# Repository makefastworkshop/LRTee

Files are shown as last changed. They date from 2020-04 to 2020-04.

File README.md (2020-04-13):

# LRTee: 3D Printed Ventilator Splitter
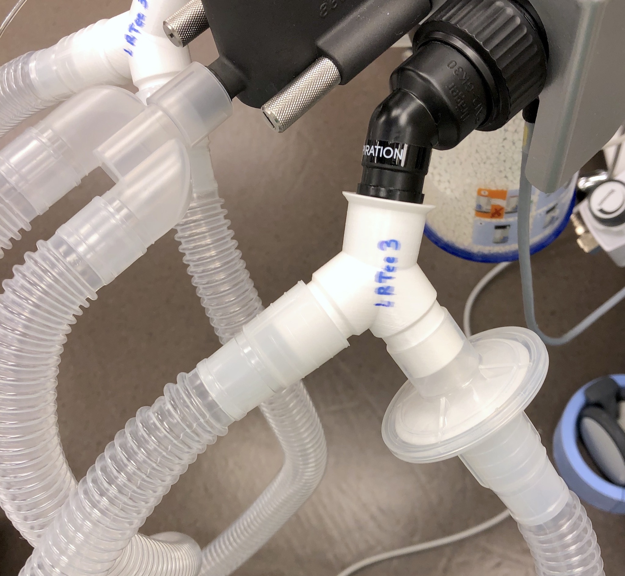
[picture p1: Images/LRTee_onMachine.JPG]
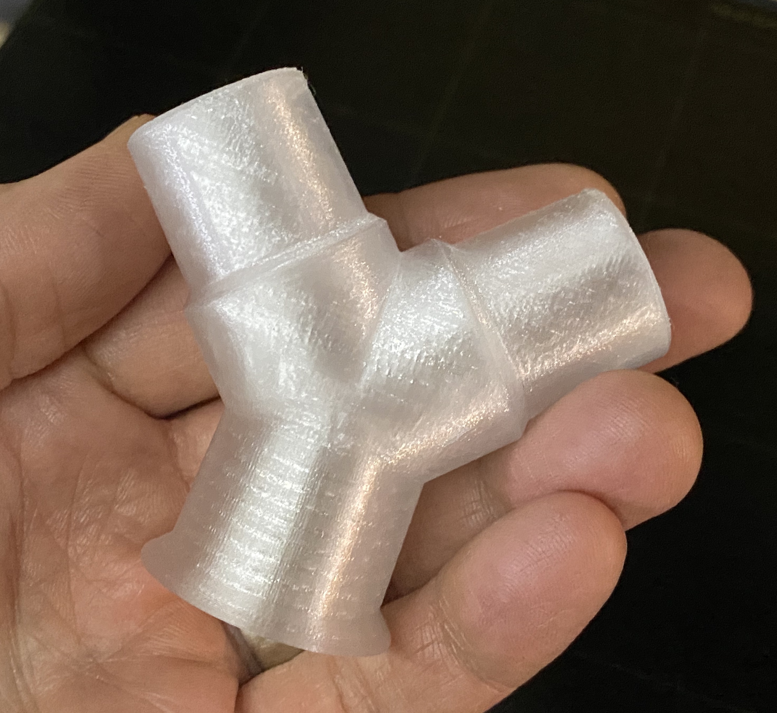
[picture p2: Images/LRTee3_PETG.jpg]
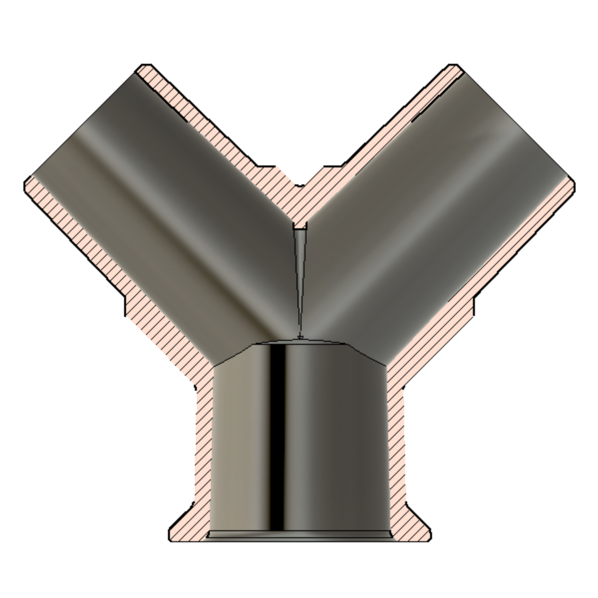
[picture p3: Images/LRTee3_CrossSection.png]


**LRTee is a 3D printed ventilator splitter** with standard 22mm tubing connectors to be used only in the event of Emergency Use Authorization when there is no more ventilator capacity.

Unlike other splitters, LRTee is designed to print on a standard FFF/FDM 3D printer without the need for supports/rafts and is optimized for creating an air-tight part that can pass a ventilator system's automated leak test without the need for post processing.

LRTee is released as public domain (Creative Commons Zero v1.0 Universal) for anyone to use, modify, share, produce, etc. with no strings attached.

## Background

Patients with COVID-19 in serious or critical condition often require assisted breathing via ventilator. As the number of patients in need of ventilators grows (exponentially in many densely populated regions), there are not adequate numbers of ventilators to support the high number of patients.

This is an EXPERIMENTAL splitter for 22m tubing to allow two patients to share a single ventilator. After printing/testing multiple versions of other splitter designs (see below) we decided to build a new splitter that:

* Has uniformly thicker walls.
* Has shorter branches (less likely to break).
* Is much faster to print (under 4 hours to print a usable pair or LRTee parts).
* Doesn't require supports or rafts.
* Can be scaled to handle basic low-temp sterilization (use 101-102% for PLA).
* **Released as Public Domain** (CC0) with all design files for further modifications.

## Disclaimer

As with other similar efforts, **THIS IS UNCERTIFIED, HIGHLY EXPERIMENTAL, and UNTESTED ON HUMANS**. As such, any potential use scenario would also require **legal waivers to use uncertified/untested non-medical devices** and **significant additional patient monitoring by medical professionals and certified diagnostic equipment** to reduce the risk of serious consequences in the event that the device fails to operate as intended by doctors. Use at your own risk. We take no responsibility for the safety of this device/design. 

These parts have been test-fit on anesthesia machines with ventilator capabilities and standard 22mm ventilator tubing/circuit connectors. The parts should be able to pass the system's automated "leak test" directly off the printer with no post-processing.

## Supplying LRTee to Hospitals

If you intend to print LRTee splitters and supply them to local hospitals, we recommend following these steps:

* First, contact the hospital by phone where you intend to supply the parts and see if they are needed/wanted as a last resort.
* Assume you are infected and act accordingly at all times (COVID-19 can be asymptomatic for some people, and protecting hospital staff is critically important). Wash hands and don't handle any more than necessary.
* Use the highest quality PETG or PLA you have. Using pure/uncolored materials is best to limit the addition of other unspecified compounds in the plastic.
* Make a test print. Depending on your printer's setup, you may need to tune settings to get the best print possible.
* Print the associated parts as specified. Note that it takes two (2) splitters for each additional patient, so it's logical to print and supply them in pairs.
* When the parts are finished, try to knock off any burrs, globs, or stringing that could interfere with their operation. You may also be able to gently fit the parts into each other and twist to get a sense for how smoothly the connectors fit.
* Place in a sealable/zip-top plastic bag.
* Print and fill out a form to help the hospital and make certain that you, as a maker trying to help, cannot be held liable (see [LRTee - Hospital Intake Printout.pdf](https://github.com/makefastworkshop/LRTee/blob/master/Docs/LRTee%20-%20Hospital%20Intake%20Printout.pdf)).
* Place signed and dated form in the bag with the parts and seal.
* Call ahead and schedule a drop off to appropriate medical personnel.

## Print Instructions

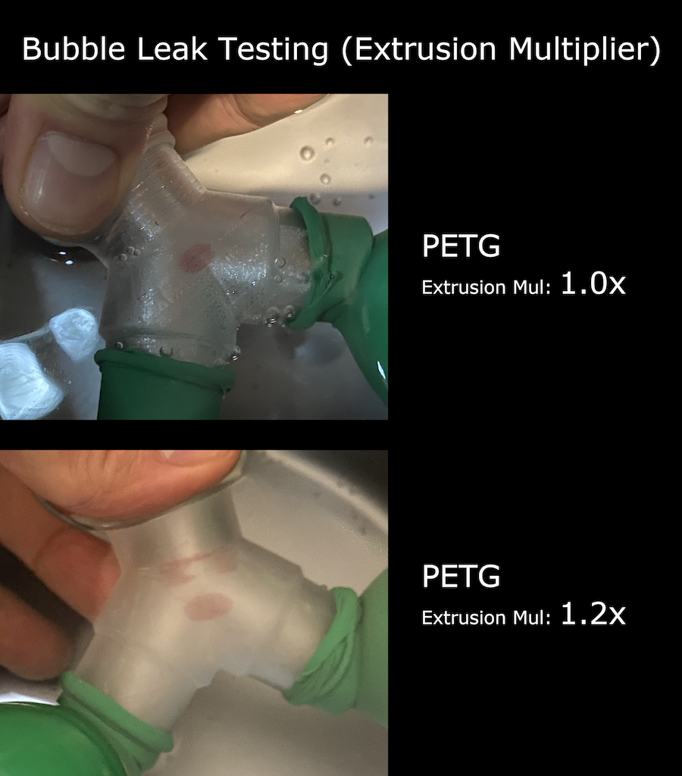
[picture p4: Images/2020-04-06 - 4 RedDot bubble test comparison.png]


This part is designed to be printed in either PETG (recommended) or PLA. When sterilized, either of these materials are likely to be usable in last-resort circumstances.

While the parts should print very cleanly, it's good to double check that all fittings are clean and free of extraneous globs of materials to ensure the best connection possible. 

The parts should be able to pass the ventilator system's automated "leak test" directly off the printer with no post-processing needed.

Infill of 100% should be achieved by using a very high number of perimeters that force smooth, solid printing throughout the build.

### Printing in PETG

Printing in natural/clear PETG is recommended due to its slightly more flexible nature, toughness, and resistance to elevated temperatures (up to 75C without significant shrinkage/warping).

We've also found that PETG seems to print slightly less air-tight than PLA, but this can be greatly improved by over-extruding. Setting the "extrusion multiplier" to 1.2x (and using the associated STL file that compensates slightly for the increased print size) produces a much more air-tight part.

### Printing in PLA

Note that PLA is harder and will shrink more (when heated/sterilized) than PETG. As such, if printed in PLA a sterilization "bath" may be preferred instead of using a low-temp sterilization machine (which seems to still get up to 60C or more) to keep the part from shrinking beyond tolerances for an air-tight fit. If a PLA part will be sterilized (for example, with a low-temp VHP machine), printing at 101-102% is suggested so that the part is properly sized after shrinking.

See the image above for a comparison of shrinkage characteristics along critical dimensions for various annealing temperatures. 

## Prior Work / Reference

The general theory of using a splitter to ventilate multiple patients is nicely spelled out in [COVID-19 How to Use One Ventilator to Save Multiple Lives](https://www.youtube.com/watch?v=uClq978oohY) and [A Single Ventilator for Multiple Simulated Patients to Meet Disaster Surge](https://onlinelibrary.wiley.com/doi/epdf/10.1197/j.aem.2006.05.009).

Thanks to these projects for informing/sharing/catalyzing design and discussion to yield a usable, printable splitter.
* [3D Printed Circuit Splitter and Flow Restriction Devices for Multiple Patient Lung Ventilation](https://www.prusaprinters.org/prints/25808-3d-printed-circuit-splitter-and-flow-restriction-d)
* [Ventilator Circuit Splitters - reinforced & thicker walls](https://www.prusaprinters.org/prints/27803-ventilator-circuit-splitters-reinforced-thicker-wa)

## Changes

**Update April 5, 2020**: More testing with annealing (via hot water bath) to simulate sterilization temperatures was performed and added as a graph (see image). Added a small rise to the lower/female lip to soften the sharp corner, and now including a PETG printer config that seems to produce good results.

**Update April 7, 2020**: We've found that PLA seems to print a bit more air-tight than PETG, but that can be greatly improved by setting the "extrusion multiplier" to 1.2x and using the modified STL file that compensates for the slightly larger dimensions when printed.

**Update April 8, 2020**: Produced 4 pairs in PETG with 1.2x extrusion multiplier and ran through the full process (from intake of printed parts at a medical facility, thorough cleaning/decontamination/sanitization, and finally testing on ventilators to verify it passes the leak test).  Parts show no sign of deformation or failure and pass all primary initial tests.

**Update April 10, 2020**: Added concise documentation to help medical facilities replicate the intake/cleaning/testing process. See the "Supplying LRTee to Hospitals" section above.

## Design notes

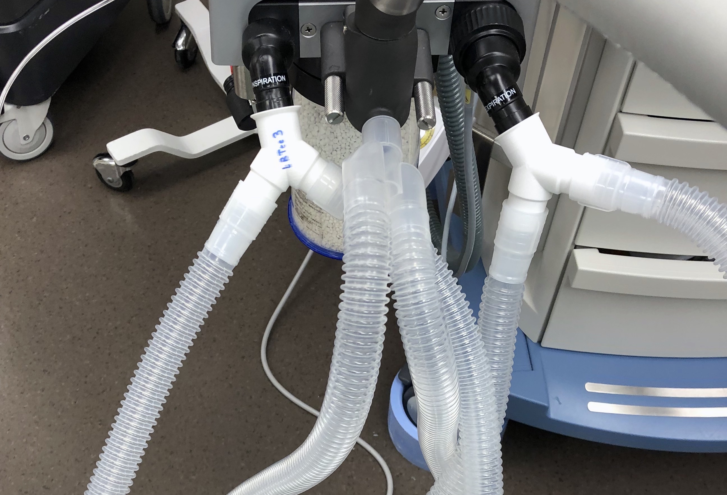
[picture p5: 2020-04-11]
Images/LRTee_onMachine2.JPG

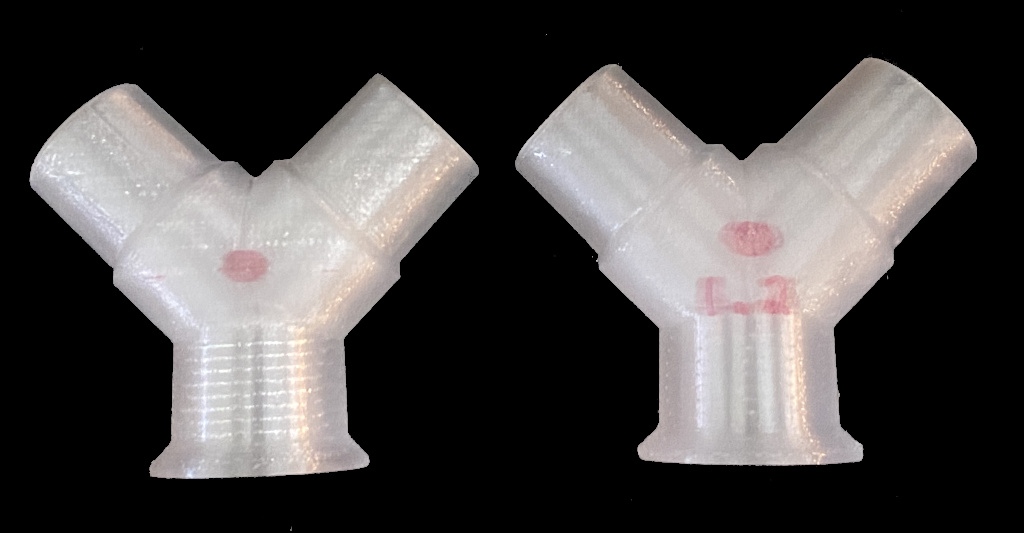
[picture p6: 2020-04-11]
Images/2020-04-06 - 1 RedDot vs OverExtrude120.jpg

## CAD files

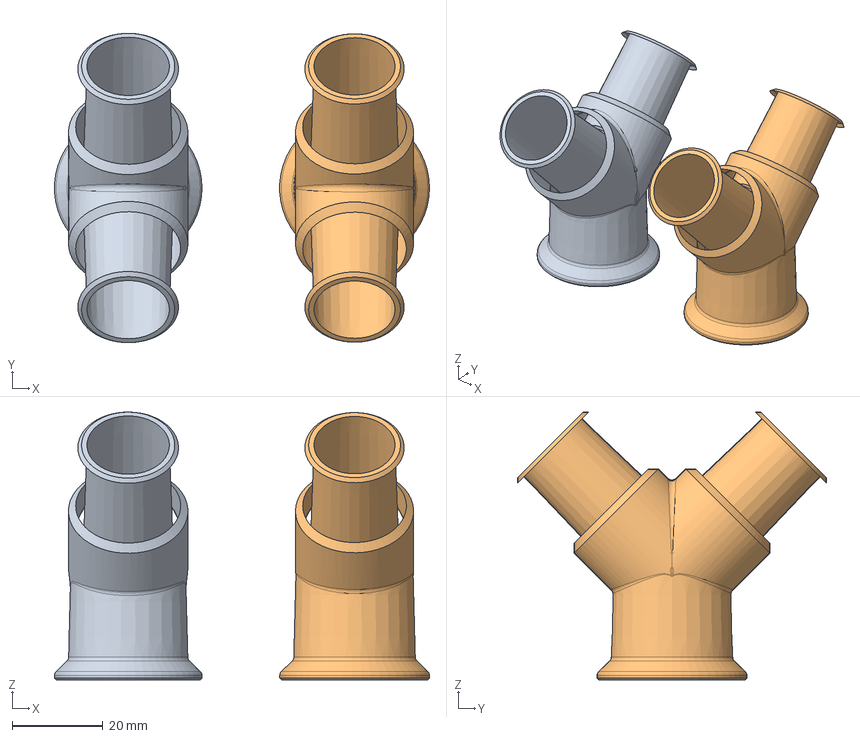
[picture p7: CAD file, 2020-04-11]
CAD/LRTee3_CAD.step
82.8 x 68.3 x 59.2 mm
LRTee3
LRTee3_ExtrudeAt1.2x

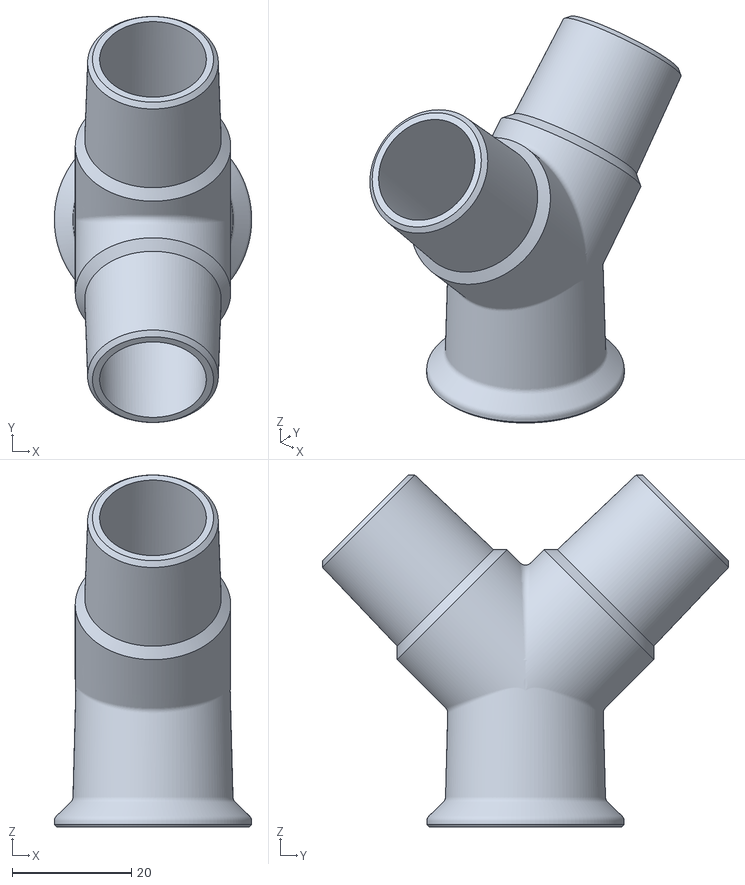
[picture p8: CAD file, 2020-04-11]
PrintFiles/LRTee3_PrintExtrudeAt12x.stl
33.1 x 68.1 x 59.1

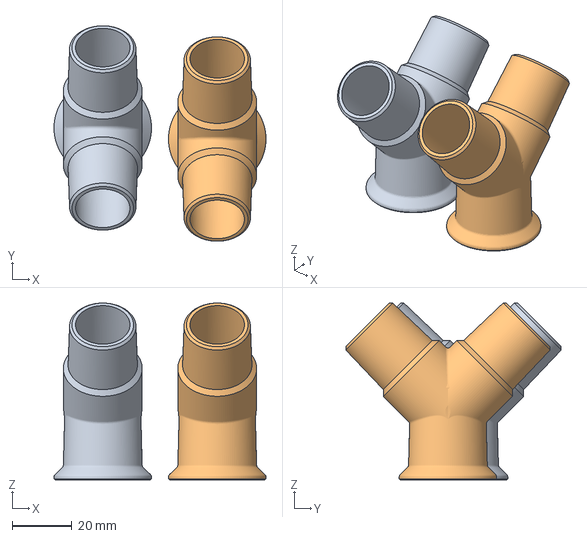
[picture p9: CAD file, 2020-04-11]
PrintFiles/LRTee3_SlicerProject_PLA_Normal.3mf
70.9 x 72.0 x 59.2 mm

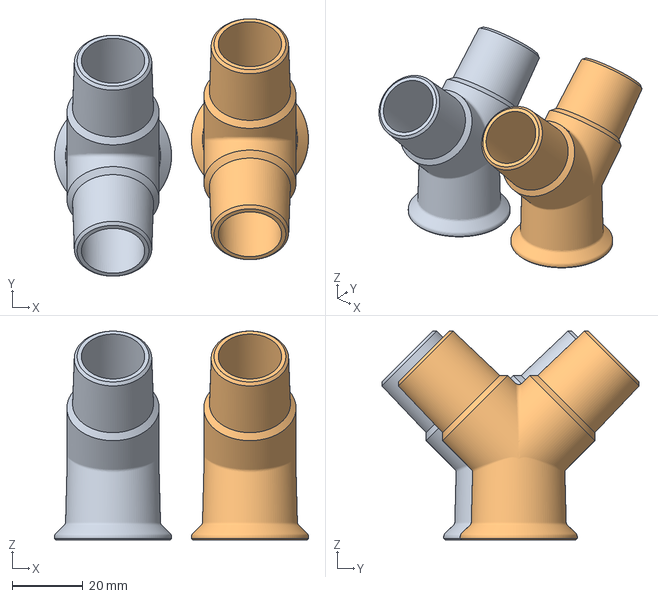
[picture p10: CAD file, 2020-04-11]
PrintFiles/LRTee3_SlicerProject_PETG_ExtrudeAt1.2x.3mf
71.8 x 72.8 x 59.1 mm

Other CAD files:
PrintFiles/LRTee3_PrintNormal.stl
CAD/LRTee3_CAD.f3d

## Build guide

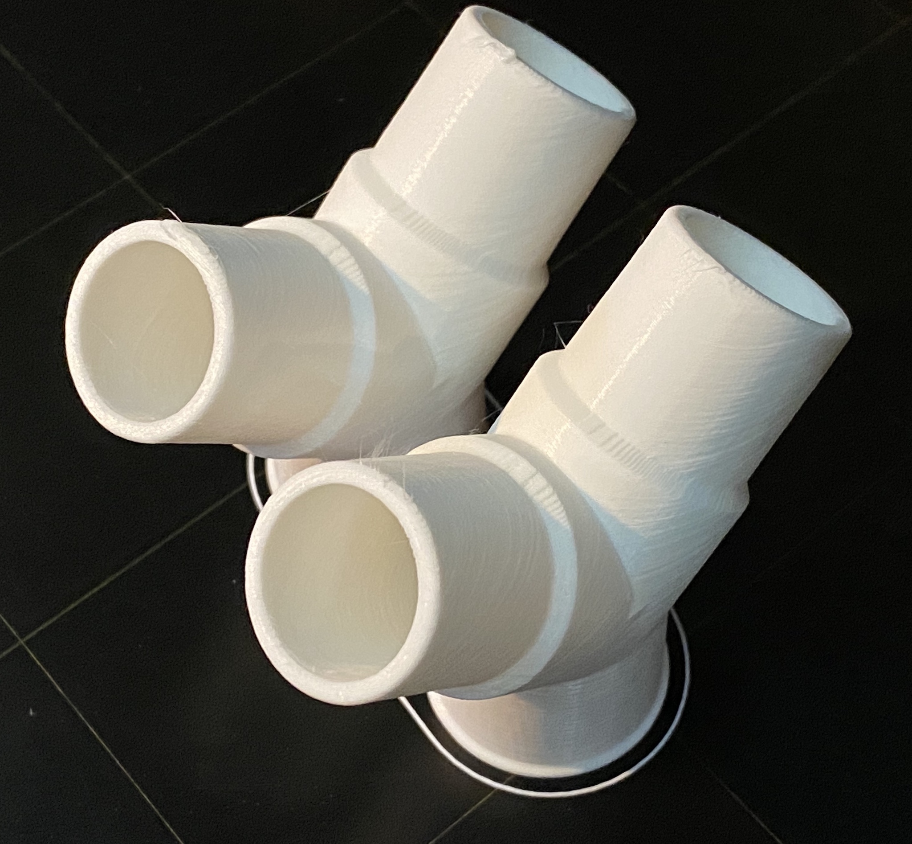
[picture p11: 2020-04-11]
Images/LRTee_printed.jpg

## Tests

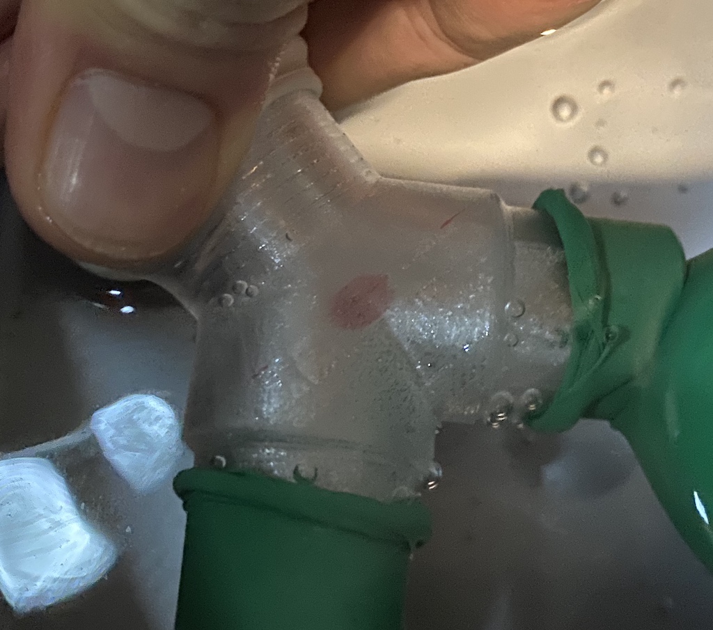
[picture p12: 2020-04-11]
Images/2020-04-06 - 2 RedDot bubble test.jpg

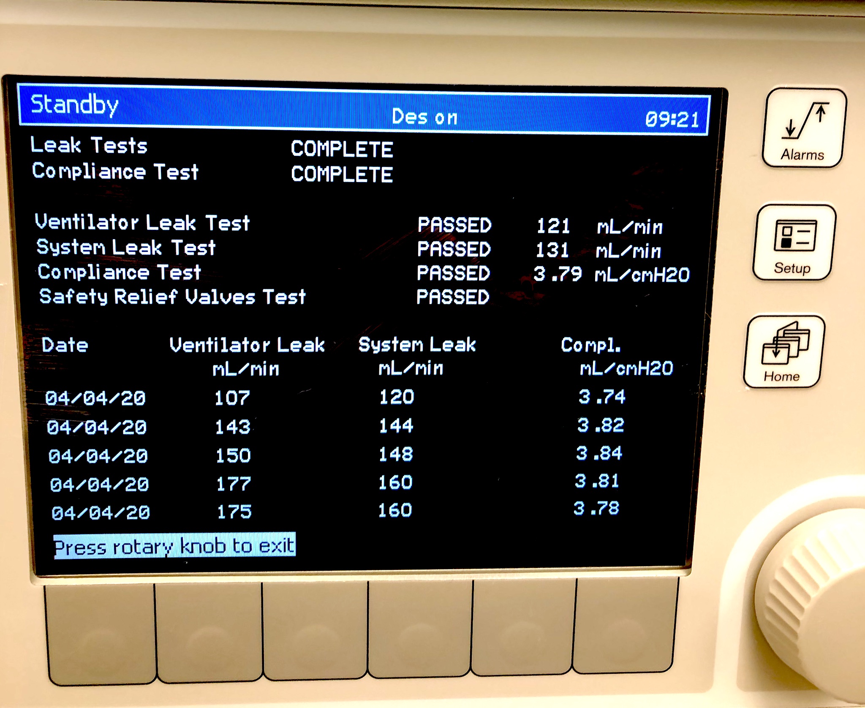
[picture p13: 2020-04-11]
Images/LRTee_passTest.JPG

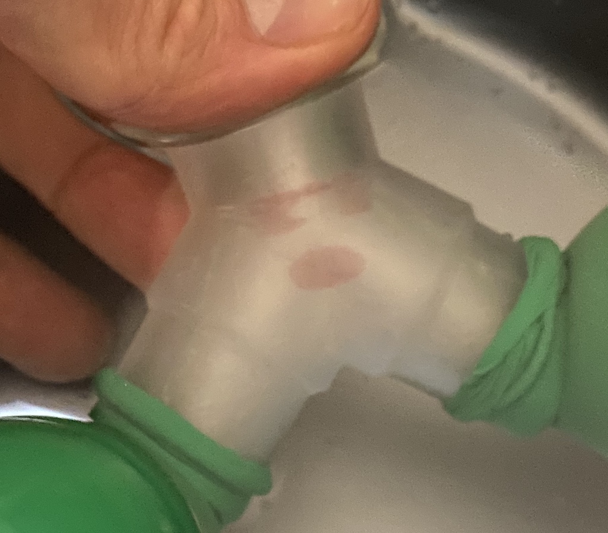
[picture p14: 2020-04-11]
Images/2020-04-06 - 3 OverExtrude bubble test.jpg
